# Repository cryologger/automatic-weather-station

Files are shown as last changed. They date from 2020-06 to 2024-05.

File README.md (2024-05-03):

<p align="left">



</p>

# Cryologger - Automatic Weather Station (AWS)

### Note: This project is under active development.


## 1.0 Introduction
Polar environments are undergoing rapid environmental change, yet there is a lack of high spatial and temporal monitoring data available in these remote regions. Reliance on expensive and proprietary commercial data acquisition and telemetry systems can inhibit both researchers and citizen scientists and present a significant barrier to the establishment of widespread monitoring networks. The development of low-cost, open-source instrumentation can greatly reduce the cost of cryospheric research, improve the spatial density and coverage of collected data, and produce new ways to observe and monitor the cryosphere.

The Cryologger Automatic Weather Station (AWS), is an open-source datalogger and telemeter comprised of low-cost, off the shelf components that is capable of supporting the physical measurement needs of a variety of cryospheric scientific applications when configured as an automatic weather station (AWS).

## 2.0 Methods

### 2.1 Design
The Cryologger AWS is based on the open-source Arduino platform (www.arduino.cc) and built using low-cost, do-it-yourself electronics that can be easily modified to meet the needs of the end-user. Code was written using the Arduino Integrated Development Environment (IDE) and benefits from the availability of community-generated libraries.

Planned for extended deployments in harsh Arctic conditions, the Cryologger AWS provides long-term measurements of weather variables such as temperature, humidity, wind speed, wind direction, solar irradiance and snow depth, as well as system diagnostic variables including pitch, roll, battery voltage. Data are transmitted over the Iridium satellite network at specified intervals and can be remotely updated based on the desired sampling frequency. Collected data are made available in near-real time at https://cryologger.org.



#### 2.1.1. Bill of Materials (BOM)

For a complete bill of materials, including requirements for power and mounting of a complete deployable system, please see ASSEMBLY.md.

**Table 1.** Bill of materials and associated costs for the main components used in the Cryologger AWS v1.0. Prices are listed in USD and are current as of December 2023. Taxes and shipping not included. <sup>1</sup>Denotes optional component.
| Component             | Product                                                                                                                      | Quantity | Cost (USD) |
|-----------------------|------------------------------------------------------------------------------------------------------------------------------|:--------:|:----------:|
| PCB                   | [Custom Cryologger Printed Circuit Board](https://jlcpcb.com)                                                                |     1    |    $5.00   |
| Satellite transceiver | [Rock7 RockBLOCK 9603](http://www.rock7mobile.com/products-rockblock-9603)                                                   |     1    |   $267.50  |
| Satellite antenna     | [Maxtena M1621HCT-P-SMA](https://maxtena.com/products/f-passive/m1621hct-p-sma-iridium-passive-antenna/)                     |     1    |   $54.00   |
| Processor             | [Adafruit Feather M0 Adalogger](https://www.adafruit.com/product/2796)                                                       |     1    |   $19.95   |
| GNSS                  | [Adafruit Ultimate GPS FeatherWing](https://www.adafruit.com/product/3133)                                                   |     1    |   $24.95   |
| IMU                   | [Adafruit LSM303AGR Accelerometer Magnetometer](https://www.adafruit.com/product/4413)                                       |     1    |   $12.50   |
| Sensor                | [Adafruit BME280 Temperature Humidity Pressure Sensor ](https://www.adafruit.com/product/2652)                               |     1    |   $14.95   |
| Voltage regulator     | [Pololu D36V6F3 3.3V 600mA Step-Down Voltage Regulator](https://www.pololu.com/product/3791)                                 |     1    |   $16.95   |
| Voltage regulator     | [Pololu D36V6F5 5V 600mA Step-Down Voltage Regulator](https://www.pololu.com/product/3792)                                   |     1    |   $16.95   |
| Voltage regulator     | [Pololu U3V40F12 12V Step-Up Voltage Regulator ](https://www.pololu.com/product/4016)                                        |     1    |    $9.95   |
| Resistor              | [10 M 1% 0.6 W resistor](https://www.mouser.ca/ProductDetail/594-MBB02070C1005FCT)                                           |     1    |    $0.44   |
| Resistor              | [1 M 1% 0.6 W resistor](https://www.mouser.ca/ProductDetail/594-B0207C1M000F5T)                                              |     1    |    $0.40   |
| Capacitor             | [0.1 uF Capacitor](https://www.mouser.ca/ProductDetail/Vishay-BC-Components/K104K15X7RF53L2?qs=mWFvmKOfYW8KbAXlf9eSQA%3D%3D) |     1    |    $0.29   |
| Power connector       |                                                                                                                              |     1    |            |
| Power connector       |                                                                                                                              |     1    |            |
| Connector             |                                                                                                                              |     1    |            |

**Table 2.** Environmental sensors used in Cryologger AWS v1.0. Prices are listed in USD and are current as of December 2023. Taxes and shipping not included.
| Environment Variable          | Sensor                                                                                                                       | Cost (USD) |
|-------------------------------|------------------------------------------------------------------------------------------------------------------------------|:----------:|
| Wind Speed & Direction        | [RM Young Wind Monitor 5103L Anemometer](https://www.youngusa.com/product/wind-monitor/)                                     | $1432      |
| Temperature/Relative Humidity | [Vaisala HMP60 Humidity and Temperature Probe](https://store.vaisala.com/en/products/HMP60)                                  | $330       |
| Solar Irradiance              | [SP-212-SS: Amplified 0-2.5 Volt Pyranometer](https://www.apogeeinstruments.com/sp-212-ss-amplified-0-2-5-volt-pyranometer/) | $325       |
| Snow Depth                    | [Maxboxtix MB7374 HRXL-MaxSonar-WRST7](https://maxbotix.com/products/mb7374)                                                 | $290       |

### 2.2 Operation
When initially powered on, the Cryologger AWS will attempt to establish a GNSS fix and sychronize the real-time clock (RTC) for up to 5 minutes. Once the RTC is synchronized, the system will set an alarm to wake at the user-specified time and then enter a low-power deep sleep. Nominally, the system will wake every 5 minutes, obtain measurements from all sensors, and log data to a microSD card. Measurements are averaged each hour and transmitted  

While the system is in deep sleep, a Watchdog Timer (WDT) will wake the system to check the program has not frozen every 8 seconds and perform a reset, if necessary. This helps to ensure the long-term reliability of the system.

#### 2.2.1 Measurements

**Table 2.** List of Cryologger AWS v1.0 data variables that can be transmitted and/or logged with variable sizes.

| Type     | Variable          | Description                        | Size (bytes) |
|----------|-------------------|------------------------------------|:------------:|
| uint32_t | unixtime          | UNIX Epoch time                    |       4      |
| int16_t  | temperatureInt    | Internal temperature (°C)          |       2      |
| uint16_t | humidityInt       | Internal humidity (%)              |       2      |
| uint16_t | pressureInt       | Internal pressure (hPa)            |       2      |
| int16_t  | temperatureExt    | External temperature (°C)          |       2      |
| uint16_t | humidityExt       | External humidity (%)              |       2      |
| int16_t  | pitch             | Pitch (°)                          |       2      |
| int16_t  | roll              | Roll (°)                           |       2      |
| uint16_t | solar             | Solar irradiance (W m-2)           |       2      |
| uint16_t | windSpeed         | Mean wind speed (m/s)              |       2      |
| uint16_t | windDirection     | Mean wind direction (°)            |       2      |
| uint16_t | windGustSpeed     | Wind gust speed (m/s)              |       2      |
| uint16_t | windGustDirection | Wind gust direction (°)            |       2      |
| int32_t  | latitude          | Latitude (DD)                      |       4      |
| int32_t  | longitude         | Longitude (DD)                     |       4      |
| uint8_t  | satellites        | Number of satellites               |       1      |
| uint16_t | hdop              | HDOP                               |       2      |
| uint16_t | voltage           | Battery voltage (V)                |       2      |
| uint16_t | transmitDuration  | Previous transmission duration (s) |       2      |
| uint8_t  | transmitStatus    | Iridium return code                |       1      |
| uint16_t | iterationCounter  | Message counter                    |       2      |

#### 2.2.2 Data Transmission and Processing

Sensor measurements and GNSS position are recorded hourly and stored in memory until the desired transmission interval is reached. Data are compressed into a binary message (340 bytes maximum) to minimize the cost and total number of transmissions required. Data are transmitted via the Iridium Short Burst Data (SBD) satellite network at user-specified intervals, which can be remotely updated based on the desired sampling frequency. SBD data messages are received by an Iridium ground station and sent to Ground Control's server. The data is then forwarded to an Amazon Web Services (AWS) SQS queue, decoded using an AWS Lambda Python function and stored in a database using the Amazon Relational Database Service (RDS). Data can be viewed in near-real time at https://cryologger.org.

## 3.0 Deployments


<p align="center"><b>Figure 3.</b> Map of Cryologger AWS deployments made between 2019 and 2023.</p>

## 4.0 Results

## 5.0 Conclusion

## Repository Contents

* **/Documentation** - Assembly, deployment and troubleshoting guides, as well as information of components used and associated costs.

* **/Hardware** - KiCad PCB schematic and design files.

* **/Software** - Arduino code and Python data analysis scripts.

## License Information
Cryologger code, firmware, and software is licensed under the GNU General Public License v3.0 (https://www.gnu.org/licenses/gpl-3.0.en.html). 

<p xmlns:cc="http://creativecommons.org/ns#" >Cryologger hardware is licensed under <a href="https://creativecommons.org/licenses/by-nc-sa/4.0/?ref=chooser-v1" target="_blank" rel="license noopener noreferrer" style="display:inline-block;">CC BY-NC-SA 4.0 </a></p>

Cheers,

**Adam**

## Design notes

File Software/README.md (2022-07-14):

# Cryologger - Automatic Weather Station: Software

## Repository Contents

* **/Arduino** - Code uploaded to the Cryologger to power the weather station.
* **/Python** - Python code used for analysis of weather data collected by the Cryologger.

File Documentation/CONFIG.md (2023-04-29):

## Sensor Configuration

### Vaisala HMP60

| Pin | Wire  | Description   | Description                    | Connector |
|:---:|:-----:|---------------|--------------------------------|:---------:|
| 1   | Brown | VDC           | Voltage Input (5-28V)          | 12V       |
| 2   | White | Channel 1: RH | Relative Humidity (%) (0-2.5V) | A3        |
| 3   | Blue  | GND           | Ground                         | GND       |
| 4   | Black | Channel 2: T  | Temperature (°C) (0-2.5V)      | A4        |
| 5   | Shield | Earth ground |                                | GND       |

#### HMP60 Configuration
See section 6.4 of the Vaisala Humidity and Temperature Probes User Guide:  
**Accessing serial line command interface from analog or Modbus mode**
https://docs.vaisala.com/r/M211060EN-L/en-US

```
# Show current output modes of analog channels
amode

# Set output modes of channels 1 & 2 to 0 - 2.5 V
amode 1 1 

# Show current output parameters and scaling
asel ?

# Change channel 1 to output relative humidity and adjust scaling to 0 to 100% and change channel 2 to temperature and adjust scaling to -60 to 40°C
asel rh t 0 100 -60 40

# Note: This can also be achieved by typing the asel command and entering values when prompted
asel

```

### RM Young 5103L Wind Monitor
| Pin | Wire   | Description                         | Connector |
|:---:|:------:|-------------------------------------|:---------:|
| 1   | White  | 12-30 VDC Input (Wind direction +)  | 12V       |
| 2   | Green  | 4-20 mA Output  (Wind direction -)  | A2        |
| 3   | Black  | 12-30 VDC Input (Wind speed +)      | 12V       |
| 4   | Red    | 4-20 mA Output  (Wind speed -)      | A1        |
| 5   | Shield | Earth ground                        | GND       |

### LSM303AGR
Orientation of sensor, when viewing enclosure from the front:

**Pitch:**
* Positive values (+) = Upwards (↑)
* Negative values (-) = Downwards (↓)

**Roll:**
* Positive values (+) = Left (←)
* Negative values (-) = Right (→)

## Amazon Web Services (AWS) Configuration

### Data Transmission Format

| Type     | Variable          | Description                    | Bytes | Encoding formula |
|----------|-------------------|--------------------------------|-------|------------------|
| uint32_t | unixtime          | UNIX Epoch time                | 4     |                  |
| int16_t  | intTemperature    | Internal temperature (°C)      | 2     | * 100            |
| int16_t  | extTemperature    | External temperature (°C)      | 2     | * 100            |
| uint16_t | extHumidity       | External humidity (%)          | 2     | * 10             |
| int16_t  | pitch             | Pitch (°)                      | 2     | * 100            |
| int16_t  | roll              | Roll (°)                       | 2     | * 100            |
| uint16_t | windSpeed         | Wind speed (m/s)               | 2     | * 100            |
| uint16_t | windDirection     | Wind direction (°)             | 2     |                  |
| uint16_t | windGust          | Wind gust speed (m/s)          | 2     | * 100            |
| uint16_t | windGustDirection | Wind gust direction (°)        | 2     |                  |
| uint16_t | voltage           | Battery voltage (V)            | 2     | * 100            |
| uint16_t | transmitDuration  | Previous transmission duration | 2     |                  |
| uint8_t  | transmitStatus    | Iridium return code            | 1     |                  |
| uint16_t | iterationCounter  | Message counter                | 2     |                  |
|          |                   |                      **Total** | **29**|                  |

### MariaDB 

```
CREATE TABLE 2022_aws_arctic_bay (id INT NOT NULL AUTO_INCREMENT PRIMARY KEY, imei BIGINT UNSIGNED, momsn INT UNSIGNED, transmit_time TEXT(24), iridium_latitude DOUBLE, iridium_longitude DOUBLE, iridium_cep DOUBLE, data TEXT(340), unixtime INT UNSIGNED, temperature_int DOUBLE, temperature_ext DOUBLE, humidity_ext DOUBLE, pitch DOUBLE, roll DOUBLE, wind_speed DOUBLE, wind_direction DOUBLE, wind_gust_speed DOUBLE, wind_gust_direction DOUBLE, voltage DOUBLE, transmit_duration SMALLINT, transmit_status TINYINT, message_counter INT UNSIGNED);
```

```
CREATE TABLE 2022_aws_pond_inlet (id INT NOT NULL AUTO_INCREMENT PRIMARY KEY, imei BIGINT UNSIGNED, momsn INT UNSIGNED, transmit_time TEXT(24), iridium_latitude DOUBLE, iridium_longitude DOUBLE, iridium_cep DOUBLE, data TEXT(340), unixtime INT UNSIGNED, temperature_int DOUBLE, temperature_ext DOUBLE, humidity_ext DOUBLE, pitch DOUBLE, roll DOUBLE, wind_speed DOUBLE, wind_direction DOUBLE, wind_gust_speed DOUBLE, wind_gust_direction DOUBLE, voltage DOUBLE, transmit_duration SMALLINT, transmit_status TINYINT, message_counter INT UNSIGNED);
```

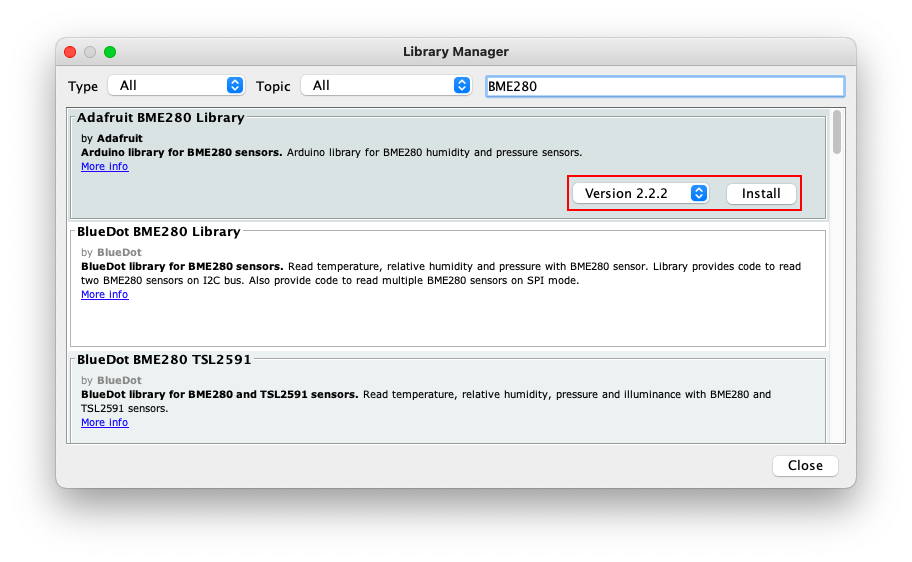
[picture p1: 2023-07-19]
Images/arduino-ide-library.png

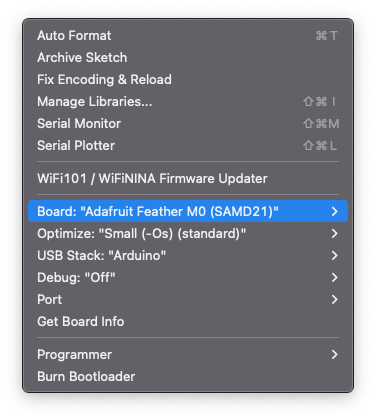
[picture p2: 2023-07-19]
Images/arduino-ide-board-1.png

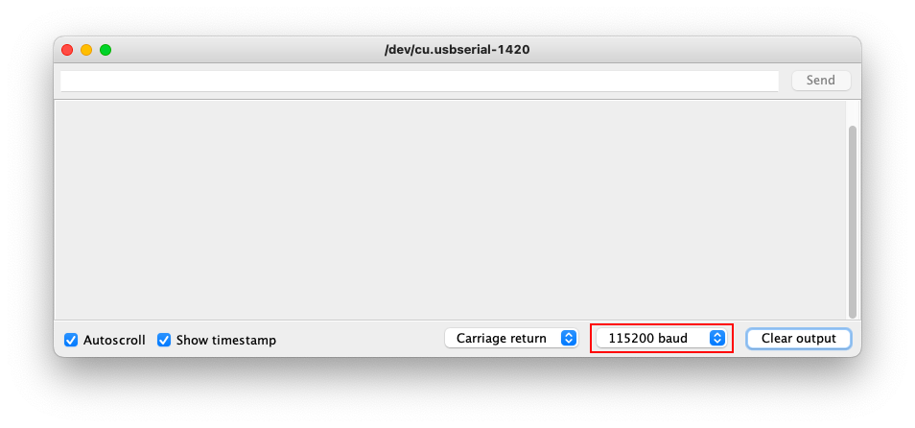
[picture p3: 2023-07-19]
Images/arduino-ide-serial-monitor-2.png

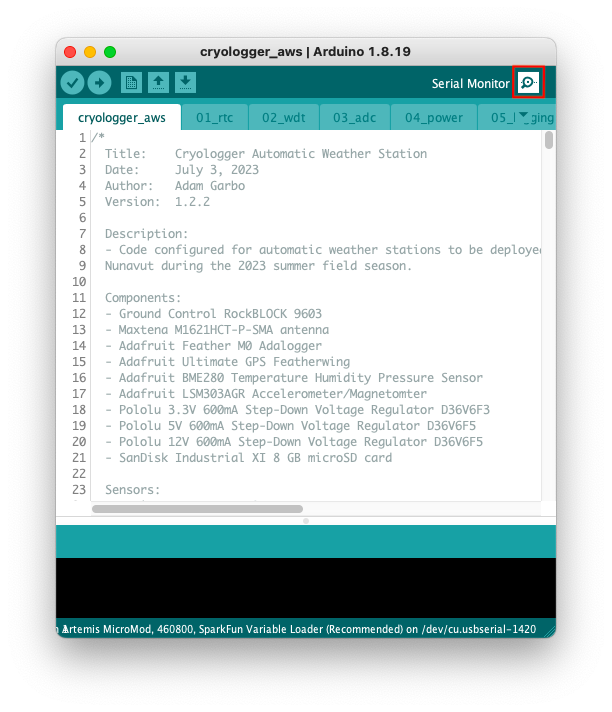
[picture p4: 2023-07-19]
Images/arduino-ide-serial-monitor-1.png

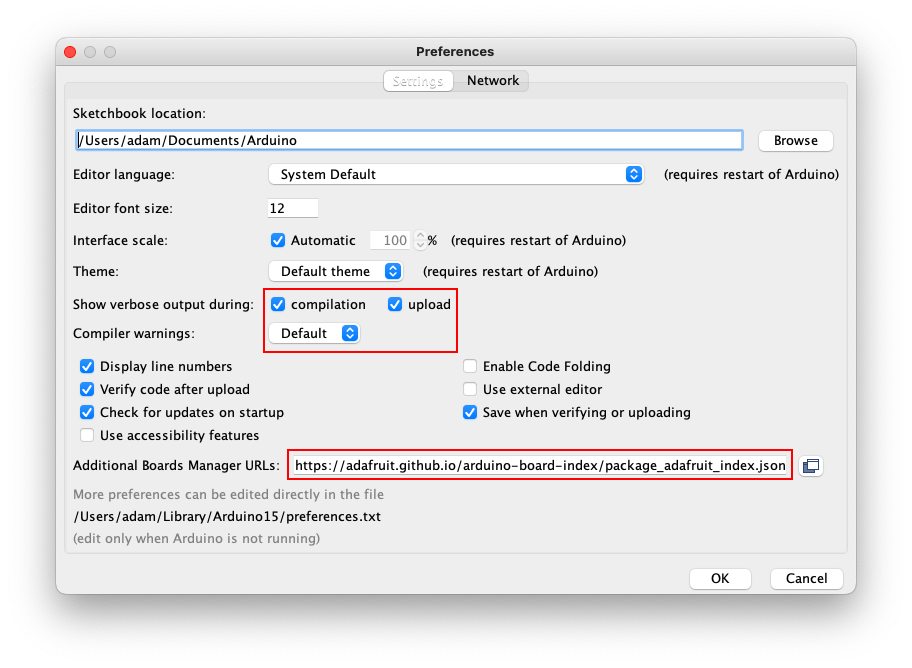
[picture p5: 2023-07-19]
Images/arduino-ide-preferences.png

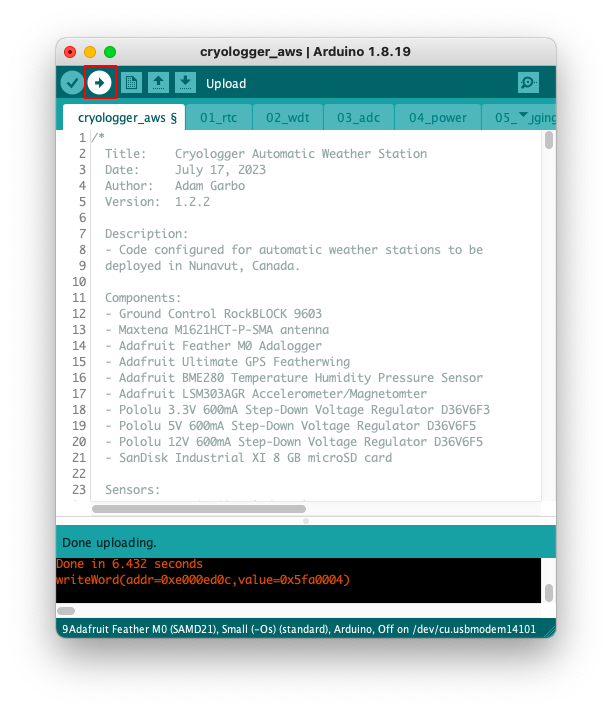
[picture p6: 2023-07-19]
Images/arduino-ide-upload.png

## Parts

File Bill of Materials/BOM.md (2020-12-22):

# Bill of Materials

| Component | Product | Cost (USD) | URL |
| --- | --- | :---: | --- |
| Satellite transceiver | Rock7 RockBLOCK 9603 | $249.95 | https://www.rock7.com/shop-product-detail?productId=51 |
| Microcontroller | Adafruit Feather M0 Adalogger | $19.95 | https://www.adafruit.com/product/2796 |
| Real-time clock | Adafruit DS3231 Precision RTC FeatherWing | $13.95 | https://www.adafruit.com/product/3028 |
| Real-time clock battery | CR1220 12mm Diameter - 3V Lithium Coin Cell Battery | $2.50 | https://www.adafruit.com/product/380 |
| Protoboard | Adafruit FeatherWing Tripler Mini Kit | $8.50 | https://www.adafruit.com/product/3417 |
| Terminal block | Adafruit Terminal Block kit for Feather - 0.1" Pitch | $5.95 | https://www.adafruit.com/product/3173 |
| Voltage Regulator | Pololu D36V6F3 3.3V 600 mA Step-Down Voltage Regulator | $4.95 | https://www.pololu.com/product/3791 |
| Power connector | Male DC Power adapter - 2.1mm plug to screw terminal block | $2.00 | https://www.adafruit.com/product/369 |
| Power connector | Breadboard-friendly 2.1mm DC barrel jack | $0.95 | https://www.adafruit.com/product/373 |
| Anemometer / Wind Vane | Davis Instruments Anemometer (#7911) | $155.00 | https://www.davisinstruments.com/product/anemometer-for-weather-monitor-or-wizard/ |
| Temperature / Relative Humidity Sensor | Davis Instruments Temperature/Humidity Sensor (#6834) | $70.00 | https://www.davisinstruments.com/product/temperature-humidity-sensor/ |
| Radiation Shield | Davis Instruments Radiation Shield (#7714) | $85.00 | https://www.davisinstruments.com/product/radiation-shield/ |
| Battery |	Tadiran	Lithium Pulses Plus 7.2V 38Ah 273.6Wh (TLP-93131/B/AL1) | $150 | http://www.tadiranbat.com/assets/tlp-93121-b-al1.pdf |
| Enclosure | Pelican 1120 | $31.95 | https://www.pelican.com/us/en/product/cases/protector/1120 |
| Total |  | $1000 | |

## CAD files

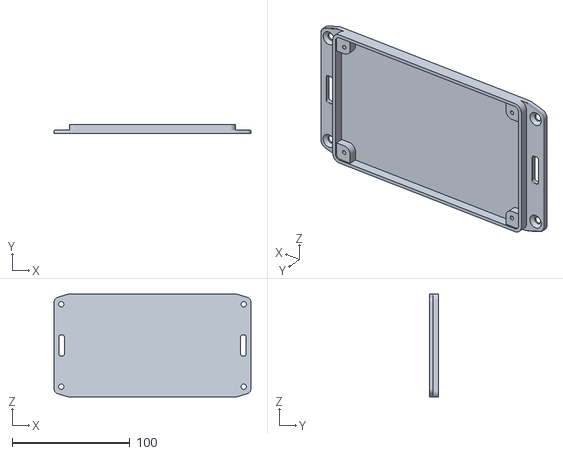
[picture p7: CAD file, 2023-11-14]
Hardware/3D Printing/Enclosure Bottom.stl
167.4 x 8.00 x 87.4

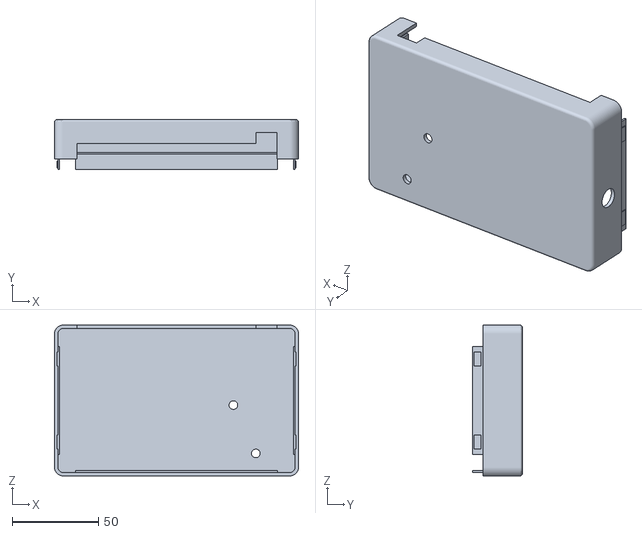
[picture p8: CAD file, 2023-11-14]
Hardware/3D Printing/Enclosure Top.stl
141.4 x 29.0 x 87.4

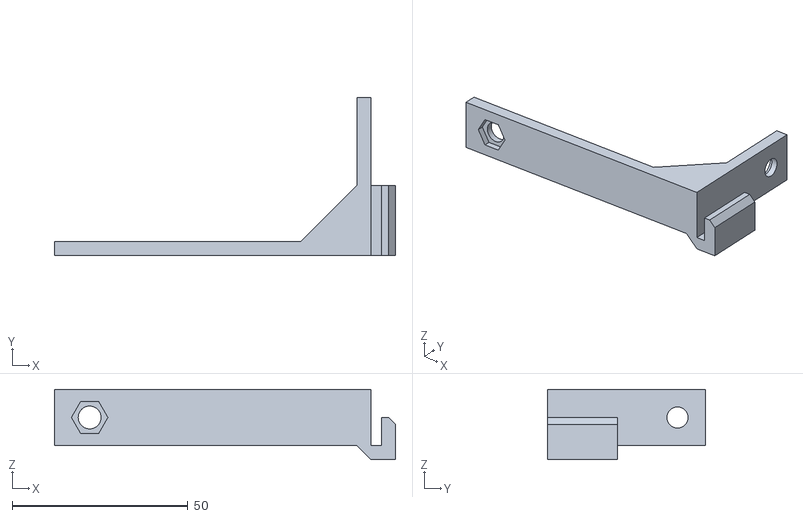
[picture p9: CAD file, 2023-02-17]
Hardware/3D Printing/Antenna Arm.stl
97.0 x 45.0 x 20.0

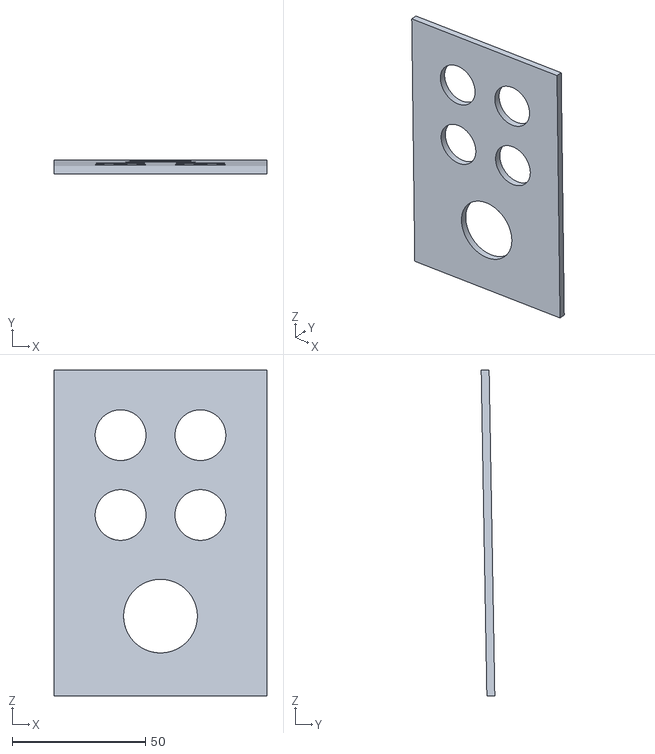
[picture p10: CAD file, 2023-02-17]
Hardware/3D Printing/Connector Panel.stl
80.0 x 5.14 x 122.5

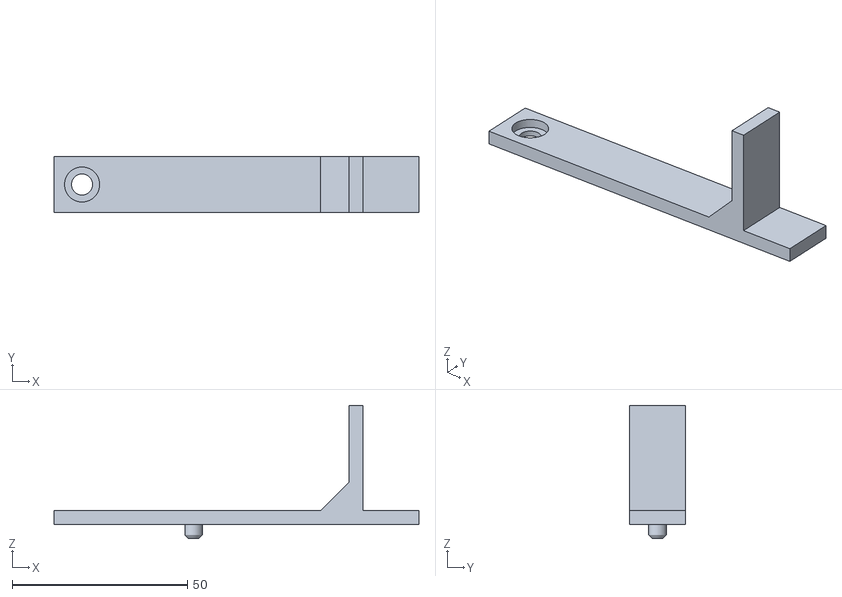
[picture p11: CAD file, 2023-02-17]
Hardware/3D Printing/Battery Bracket.stl
104.0 x 16.0 x 38.0

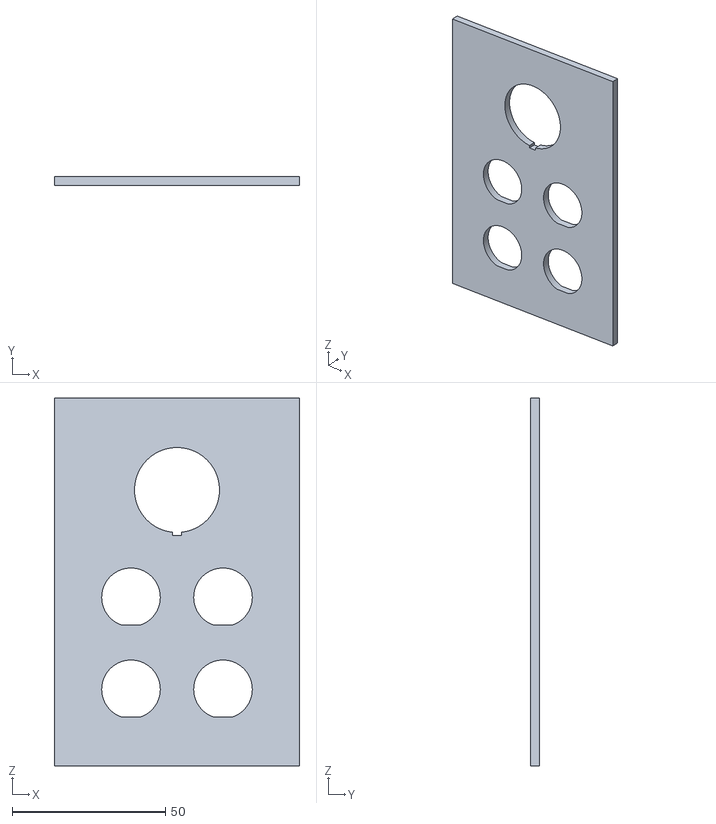
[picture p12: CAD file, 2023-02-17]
Hardware/3D Printing/Connector Panel Keyed.stl
80.0 x 3.00 x 120.0

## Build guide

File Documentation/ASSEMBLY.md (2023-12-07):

# Cryologger Automatic Weather Station (AWS) - Assembly

## 1.0 Introduction
This guide provides detailed instructions on the assembly of a Cryologger AWS v1.0.

## 2.0 Bill of Materials (BOM)
The components required to assemble a Cryologger GVT system are split into two groups: 
1) Components required for the assembly of the Cryologger AWS (e.g., PCB, GNSS receiver, microcontroller, etc.)
2) Components required for the mounting, power and deployment of the complete system (e.g., tripod, solar panel, battery, etc.).

**Table 1.** Recommended tools required for the asssembly of a Cryologger AWS v1.0.
| Tool | Recommended Product |
| --- | --- | 
| Soldering iron | [Hakko FX-888D Digital Soldering Station](https://hakkousa.com/fx-888d-digital-soldering-station.html) |
| Solder | [SparkFun Solder - 1/4lb Spool (0.020") Special Blend](https://www.sparkfun.com/products/10242) |
| Side cutter | [Hakko CHP-170 Micro Cutter](https://hakkousa.com/chp-170-micro-cutter.html) |
| Pliers | [Hakko CHP PN-2001 Pointed Nose Pliers](https://hakkousa.com/products/chp-tools/chp-hand-tools/chp-pn-2001-pointed-nose-pliers.html) |
| Hot-air rework station | [Quick 957DW+](https://www.adafruit.com/product/1869) |
| Screw driver | Phillips head screw driver |
| PCB cleaning brush | [ESD-Safe PCB Cleaning Brush](https://www.adafruit.com/product/1209) |
| PCB cleaning solution | Deionized (DI) water |

**Table 1.** Bill of materials and associated costs for components used in the Cryologger AWS v1.0. Prices are listed in USD and are current as of December 2023. Taxes and shipping not included. <sup>1</sup>Denotes optional component. Please note the BOM is a work in progress.
| Component             | Product                                                               | Cost (USD) |
|-----------------------|-----------------------------------------------------------| :---: |
| Satellite transceiver | [Rock7 RockBLOCK 9603](http://www.rock7mobile.com/products-rockblock-9603) | $267.50
| Satellite antenna*    | [Maxtena M1621HCT-P-SMA](https://maxtena.com/products/f-passive/m1621hct-p-sma-iridium-passive-antenna/) | $54.00 
| Processor             | [Adafruit Feather M0 Adalogger](https://www.adafruit.com/product/2796) | $19.95
| GNSS                  | [Adafruit Ultimate GPS FeatherWing](https://www.adafruit.com/product/3133) | $24.95
| IMU                   | [Adafruit LSM303AGR Accelerometer Magnetometer](https://www.adafruit.com/product/4413) | $12.50
| Sensor                | [Adafruit BME280 Temperature Humidity Pressure Sensor ](https://www.adafruit.com/product/2652) | $14.95
| Voltage regulator     | [Pololu D36V6F3 3.3V 600mA Step-Down Voltage Regulator](https://www.pololu.com/product/3791) | $16.95 
| Voltage regulator     | [Pololu D36V6F5 5V 600mA Step-Down Voltage Regulator](https://www.pololu.com/product/3792) | $16.95 
| Voltage regulator     | [Pololu U3V40F12 12V Step-Up Voltage Regulator ](https://www.pololu.com/product/4016) | $9.95 
| Resistor              | [10 M 1% 0.6 W resistor](https://www.mouser.ca/ProductDetail/594-MBB02070C1005FCT) | $0.44 |
| Resistor              | [1 M 1% 0.6 W resistor](https://www.mouser.ca/ProductDetail/594-B0207C1M000F5T) | $0.40 
| Capacitor             | [0.1 uF Capacitor](https://www.mouser.ca/ProductDetail/Vishay-BC-Components/K104K15X7RF53L2?qs=mWFvmKOfYW8KbAXlf9eSQA%3D%3D) | $0.29 
| Power connector       |	[Phoenix Contact MSTB 2,5/ 2-ST-5,08 - 1757019](https://www.mouser.ca/ProductDetail/Phoenix-Contact/1757242?qs=%2Fha2pyFadugVjodGKkrF4xNq%252BZEVHysqCHlL2cTnJ%252B8%3D) | $0.67 
| Power connector	      | [Phoenix Contact MSTBA 2,5/ 2-G-5,08 - 1757242](https://www.mouser.ca/ProductDetail/Phoenix-Contact/1757019?qs=sGAEpiMZZMvlX3nhDDO4AGmxTE5dWGQY3FmaBdjJUN0%3D) | $2.08 
| Connector             |	[Molex PicoBlade PCB Header](https://www.mouser.ca/datasheet/2/276/0530471010_PCB_HEADERS-171035.pdf) | $0.50 

**Table x.** Sensors
| Environment Variable          | Sensor                                                                                         | Cost (USD) |
|-------------------------------|------------------------------------------------------------------------------------------------|:----------:|
| Wind Speed & Direction        | [RM Young Wind Monitor 5103L Anemometer](https://www.youngusa.com/product/wind-monitor/)       | $1432      |
| Temperature/Relative Humidity | [Vaisala HMP60 Humidity and Temperature Probe](https://store.vaisala.com/en/products/HMP60)    | $330       |
| Solar Irradiance              | [SP-212-SS: Amplified 0-2.5 Volt Pyranometer](https://www.apogeeinstruments.com/sp-212-ss-amplified-0-2-5-volt-pyranometer/) | $325       |
| Snow Depth                    | [Maxboxtix MB7374 HRXL-MaxSonar-WRST7](https://maxbotix.com/products/mb7374)                   | $290       |

**Table 3.** Components making up the enclosure, mounting and power systems for Cryologger AWS v1.0. <sup>1</sup>Denotes optional component. <sup>2</sup>Denotes educational pricing.
| Component | Product | Quantity | Cost (USD) | 
| --- | --- | :---: | :---: | 
| Solar Panel | [Ameresco Solar 20 Watt Solar Panel 20J<sup>2</sup>](https://www.amerescosolar.com/20j-ameresco-solar-20-watt-solar-panel) | 1 |  $99.00 |
| Solar Panel Bracket | [Ameresco Solar HPM18-30 Solar Panel Pole Mount<sup>2</sup>](https://www.amerescosolar.com/hpm18-30solar-panel-pole-mount) | 1 |  $39.00 
| Solar Charge Controller | [Genasun GV-4 4A MPPT Solar Charge Controller](https://www.altestore.com/store/charge-controllers/solar-charge-controllers/mppt-solar-charge-controllers/genasun-gv-4-pb-12v-4a-mppt-controller-for-12v-lead-acid-batteries-p10622/) | 1 |  $63.00 |
| Solar Panel Power Cable | [Polarwire Arctic Ultraflex Blue Twin Trailer Cable AUF-TC162](https://store.polarwire.com/arctic-trailer-cable-16-2-gray-16ga-2-conductors/) | Variable | $0.55/ft |
| Solar Panel Cable Gland | [Heyco M4340 M20 Cable Gland](https://octopart.com/m4340-heyco-2298364?r=sp) | 2 | $5.94 |
| Battery Ring Terminal | [Molex Perma-Seal Ring Terminal 14-16 AWG Wire 1/4" (M6) 19164-0026](https://octopart.com/19164-0026-molex-99569?r=sp) | 2 | $1.00 |
| Battery | Deka SOLAR Gel 48 Ah 8G40C | 1 | ~$150.00 |
| Antenna Bulkhead Adapter | [Amphenol TNC Jk to TNC Jk 50 Ohm Str Bkhd IP67 AD-TNCJTNCJ-1](https://octopart.com/ad-tncjtncj-1-amphenol+rf-108109770?r=sp) | 1 | $42.79 |
| Antenna Cable | [GPAC GPS Antenna Cable TNC to TNC (3 m)](https://www.gpac-llc.com/product.php?product=1) | 1 | $56.00 |
| Enclosure | [L-Com 14x12x7 Inch Weatherproof NEMA Enclosure](https://www.l-com.com/nema-enclosures-14x12x7-inch-weatherproof-nema-enclosure-only) | 1 |  $161.99 |
| Enclosure Panel | [L-Com Blank Aluminum Mounting Plate](https://www.l-com.com/nema-enclosures-blank-aluminum-mounting-plate-for-1412xx-series-enclosures) | 1 |  $32.39 |
| Pole Mount | [L-Com Enclosure Pole Mounting Kit](https://www.l-com.com/nema-enclosures-enclosure-pole-mounting-kit-pole-diameters-1-1-4-to-2-inches) | 1 | $75.99 |
| Tripod | [Onset HOBO Weather Station m 3m Tripod M-TPA](https://www.onsetcomp.com/products/mounting/m-tpa/) | 1 |  $200.00 | 

## 3.0 Assembly

### 3.1 Cryologger AWS PCB Assembly
**1) Collect all required components**
* It is suggested to first gather all of the components listed in the bill of materials (Table 2), required for the assembly of the Cryologger. Remove the components from their packaging and inspect them for any signs of damage.

**2) Solder through-hole resistors and capacitor**
* The first components recommended to be soldered to the Cryologger PCB are the through-hole resistors and capacitor (Figure 1). 
* Both the capacitor and resistors can be inserted into the PCB in any orientation.
* It is important to pay attention to the placement of the resistors, as they differ in resistance. 
  * R1 = 10 MOhm. Colour code: Brown Black Black Green Brown
  * R2 = 1 MOhm. Colour code: Brown Black Black Yellow Brown
* For more information on resistance colour codes, please see: https://www.digikey.com/en/resources/conversion-calculators/conversion-calculator-resistor-color-code

## 4.0 Calibration

## 5.0 Testing

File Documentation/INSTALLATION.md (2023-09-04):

# Cryologger Automatic Weather Station (AWS) - Installation
This guide provides step-by-step instructions on installing the Arduino IDE and required board definitions and libraries, which are necessary for uploading code to the Cryologger AWS.

## Step 1: Download Arduino IDE  
* Navigate to https://www.arduino.cc/en/software and download the Legacy 1.8.x version of the Arduino IDE
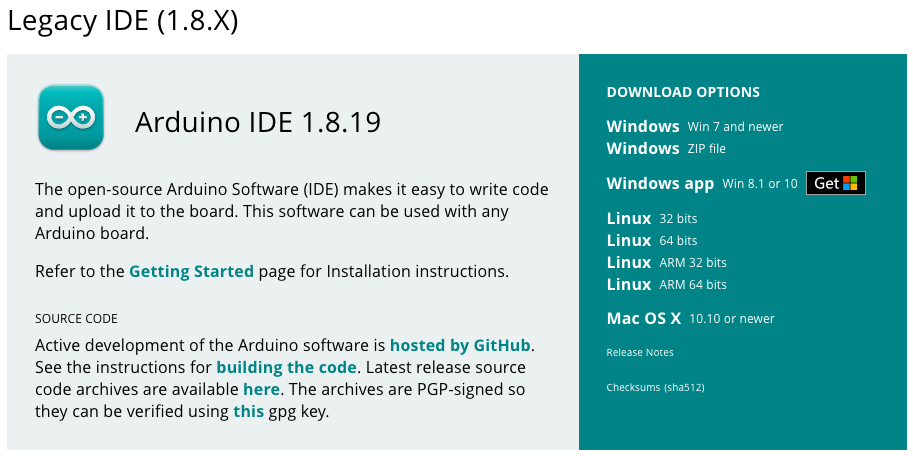
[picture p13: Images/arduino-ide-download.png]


## Step 2: Add Additional Boards Manager URL:
* In the Arduino IDE navigate to: Preferences
* Add the following "Additional Boards Manager URL" as shown in the screenshot below:  
```https://adafruit.github.io/arduino-board-index/package_adafruit_index.json```
* Also during this step, check the "compile" and "upload" boxes for "Show verbose output during" and change "Compiler warnings" to "Default"
![image](/Images/arduino-ide-preferences.png)

## Step 3: Install Board Definitions
* Navigate to: Tools > Boards > Boards Manager
* Search for: SAMD Boards
* Select and install version: Arduino SAMD Boards v1.8.13 
* Select and install version: Adafruit SAMD Boards v1.7.13
![image](/Images/arduino-ide-boards.png)

## Step 4: Install Libraries
Several libraries are required by the Cryologger AWS. These can be downloaded using the Arduino IDE's Library Manager (requires an Internet connection).

* Navigate to: Tools > Manage Libraries
* Search for and install the following libraries:

**Table 1.** Libraries required by Cryologger AWS. Last updated 2023-07-01.
| Library                                         | Version | GitHub Repository                                                   |
|-------------------------------------------------|:-------:|---------------------------------------------------------------------|
| Adafruit BME280 Library                         |  2.2.2  | https://github.com/adafruit/Adafruit_BME280                         |
| Adafruit LSM303 Accelerometer Library           |  1.1.6  | https://github.com/adafruit/Adafruit_LSM303_Accel                   |
| Adafruit Unified Sensor Driver                  |  1.1.9  | https://github.com/adafruit/Adafruit_Sensor                         |
| Arduino Low Power Library                       |  1.2.2  | https://github.com/arduino-libraries/ArduinoLowPower                |
| SparkFun IridiumSBD I2C Arduino Library         |  3.0.6  | https://github.com/sparkfun/SparkFun_IridiumSBD_I2C_Arduino_Library |
| RTCZero Library                                 |  1.6.0  | https://github.com/arduino-libraries/RTCZero                        |
| SdFat                                           |  2.2.2  | https://github.com/greiman/SdFat                                    |
| Sensirion Temperature / Humidity Sensor Library |         | https://github.com/HydroSense/sensirion                             |
| Statistic Library                               |  1.0.4  | https://github.com/RobTillaart/Statistic                            |
| Arduino Time Library                            |  1.6.1  | https://github.com/PaulStoffregen/Time                              |
| TinyGPSPlus                                     |  1.0.3  | https://github.com/mikalhart/TinyGPSPlus                            |

![image](/Images/arduino-ide-library.png)

## Step 5: Download Software
Code for the Cryologger AWS is made available on the following GitHub repository:
* [https://github.com/adamgarbo/Cryologger Automatic Weather Station](https://github.com/adamgarbo/Cryologger_Automatic_Weather_Station)
* Click on "Releases" and download the .zip file of the most recent release:
![image](https://github.com/adamgarbo/cryologger-automatic-weather-station/assets/22924092/7f80eec5-b06e-466e-aa5a-90dcd1c81258)

## Step 6: Test Program Compilation
* Navigate to the /Software/Arduino/cryologger_aws folder of the downloaded repository
* Double-click on the `cryologger_aws.ino` file
* Click on the checkmark in the upper left corner of the Arduino IDE program window
* Watch debugging window for compilation errors

![image](/Images/arduino-ide-verify.png)

## Step 7: Connect Hardware & Configure Port Settings
* Connect to the Cryologger AWS using a micro USB cable.
* In the Arduino IDE click on Tools > Board > Adafruit SAMD > Adafruit Feather M0 (SAMD)

![image](/Images/arduino-ide-board-1.png)
![image](/Images/arduino-ide-board-2.png)
![image](/Images/arduino-ide-board-3.png)

* Next, click on Tools > Port and select the appropriate serial port for the Adafruit Feather M0 Adalogger
![image](/Images/arduino-ide-port-1.png)
![image](/Images/arduino-ide-port-2.png)

## Step 8: Upload Program
* Once the code has compiled successfully, click on the right-pointed arrow to upload the code
* Watch the output window for compilation errors and/or success messages
* If no errors are presented, the code has now been successfully uploaded! 
![image](/Images/arduino-ide-upload.png)

## Step 9: Observe Serial Monitor
* After successfully uploading the program, click on the magnifying glass in the top right-hand corner to open the Serial Monitor
* Click on the baud dropdown and select 115200 baud
* Ensure the data logging mode and settings are correct
![image](/Images/arduino-ide-serial-monitor-1.png)
![image](/Images/arduino-ide-serial-monitor-2.png)

## Step 10: Next Steps
* The detailed operation of the Cryologger AWS will be covered next in OPERATION.md

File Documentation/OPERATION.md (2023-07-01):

# Cryologger Automatic Weather Station (AWS) - Operation

## Wiring Diagram

**Table 1.** Davis Instruments 7911 anemometer.
| Wire   | Description    | Pin |
|--------|----------------|-----|
| Black  | Wind speed     | A1  |
| Red    | Ground         | GND |
| Green  | Wind direction | A2  |
| Yellow | Power          | U3  |

**Table 2.** Davis Instruments temperature relative humidity sensor (Sensiron SHT31-LSS).
| Wire   | Description | Pin |
|--------|-------------|-----|
| Blue   | Data        | SDA |
| Yellow | Power       | 3.3 |
| Green  | Ground      | GND |
| White  | Clock       | SCL |

**Table 3.** Wiring diagram for Apogee SP-212 pyranometer.
| Wire   | Description | Pin |
|--------|-------------|-----|
| Black  | Ground      | GND |
| White  | Sensor      | A3  |
| Red    | Power       | 5V  |
| Shield | Shield      | GND |

**Table 4.** Wiring diagram for MaxBotix MB7354 HRXL-MaxSonar-WRS5 ultrasonic sensor.
| Wire Colour |      Description      |      Pin      |
|:-----------:|:---------------------:|:-------------:|
|    White    |   Temperature Sensor  | Not connected |
|    Orange   |   Pulse Width Output  |       A3      |
|    Brown    | Analog Voltage Output | Not connected |
|    Green    |   Ranging Start/Stop  | Not connected |
|     Blue    |     Serial Output     | Not connected |
|     Red     |          Vcc          |       5V      |
|    Black    |         Ground        |      GND      |

## LED Blink Patterns

When initially powered on, the system will attempt to establish a GNSS fix and synchronize the real-time clock (RTC) for up to 2 minutes. During this time, the LED will blink every second. Once the RTC is synchronized, the system will set an alarm to wake at the user-specified time and then enter a low-power deep sleep. While the system is in deep sleep, the Watchdog Timer (WDT) will wake the system to check the program has not frozen approximately every 8 seconds. The LED will blink briefly (100 ms) during this time.

Table x. LED blink patterns and associated description and troubleshooting guide.
| Number | Duration (ms) |    Colour   |   Pattern   | Description                     | Troubleshooting Steps                     |
|:------:|:-------------:|:-----------:|:-----------:|---------------------------------|-------------------------------------------|
|    4   |      500      |     Red     |   Single    | System start up                 | None                                      |
|   10   |      100      | Green + Red | Alternating | Initialization complete         | None                                      |
|    2   |      250      |     Red     |  Continuous | microSD failure                 | Reseat microSD card and reboot system     |
|    1   |      1000     |    Green    |  Continuous | GNSS signal acquisition         | None                                      |
|    5   |      100      |    Green    |   Single    | GNSS fix found                  | None                                      |
|    5   |      100      |     Red     |   Single    | GNSS fix not found              | Ensure good view of sky                   |
|    1   |      1000     |    Green    |  Continuous | Iridium transmission attempt    | None                                      |
|   10   |      250      |    Green    |   Single    | Iridium transmission successful | None                                      |
|   10   |      250      |     Red     |   Single    | Iridium transmission failure    | Ensure good view of sky and reboot system |
|    1   |      100      |     Red     |   Single    | Watchdog Timer every 8 seconds  | None                                      |

## Tools
| Component                             	| Type                       	| Tool(s)                             	|
|---------------------------------------	|----------------------------	|-------------------------------------	|
| Enclosure panel                       	| 10/32" 3/8" Pan Head Screw 	| Phillips Head Screwdriver (large)   	|
| Enclosure pole mount bracket          	| 1/4"-20 Pan Head Screw     	| Phillips Head Screwdriver (large)   	|
| Enclosure pole mount bracket          	| 1/4"-20 Hex Nut            	| 7/16" socket/wrench                 	|
| Enclosure pole mount bracket u-bolt   	| 1/4"-20 Hex Nut            	| 7/16" socket/wrench                 	|
| Radiation shield                      	| 1/4"-20 Locknut            	| 7/16" socket                        	|
| Solar panel 1 3/4" u-bolt             	| 5/16"-18 Hex Nut           	| 1/2" wrench/socket                  	|
| Polar Wire cable                      	| 14 AWG                     	| Wire stripper                       	|
| Genasun GV-4 Solar charge controller  	| Screw terminal             	| Flat head (small)                   	|
| Deka 8GUIH battery terminals          	| 1/4"-20 Hex Nut            	| 7/16" socket/wrench                 	|
| Anemometer 1-3/4" & 1-5/8" u-bolts    	| 5/16"-18 Hex Nut           	| 1/2" socket/wrench                  	|
| Anemometer stainless steel hose clamp 	| Screw                      	| Phillips Head Screwdriver  (medium) 	|
| Anemometer stainless steel hose clamp 	| Nut                        	| 5/16" socket (optional)             	|
| Tripod 1-3/4" u-bolt                  	| 5/16"-18 Hex Nut           	| 1/2" socket/wrench                  	|
| Tripod 1-5/8" u-bolt                  	| 1/4"-20 Hex Nut            	| 7/16" socket/wrench                 	|
| Tripod guy wire kit                   	| Cable                      	| Lineman Cutters                     	|
| Tripod guy wire kit                   	| 10/32" 3/8" Pan Head Screw 	| Phillips Head Screwdriver (medium)  	|
| Tripod guy wire kit                   	| 1/4"-20 Hex Nut            	| 7/16" socket                        	|
| Tripod guy wire kit                   	| 5/16"-18 Hex Nut           	| 1/2" wrench                         	|
| PCB Screw terminals                   	| Screw terminal             	| Flat head (small)                   	|

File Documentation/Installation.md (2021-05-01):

# Installation

## Arduino IDE

Download the most recent version of the Arduino Software (IDE) from:
https://www.arduino.cc/en/main/software

### Custom Board Manager URLs:

To make use of SparkFun and Adafruit flavoured boards, it is necessary to first add their Additional Boards Manager URLs. These are JSON URLs added as a comma-separated list in Preferences of the Arduino IDE.

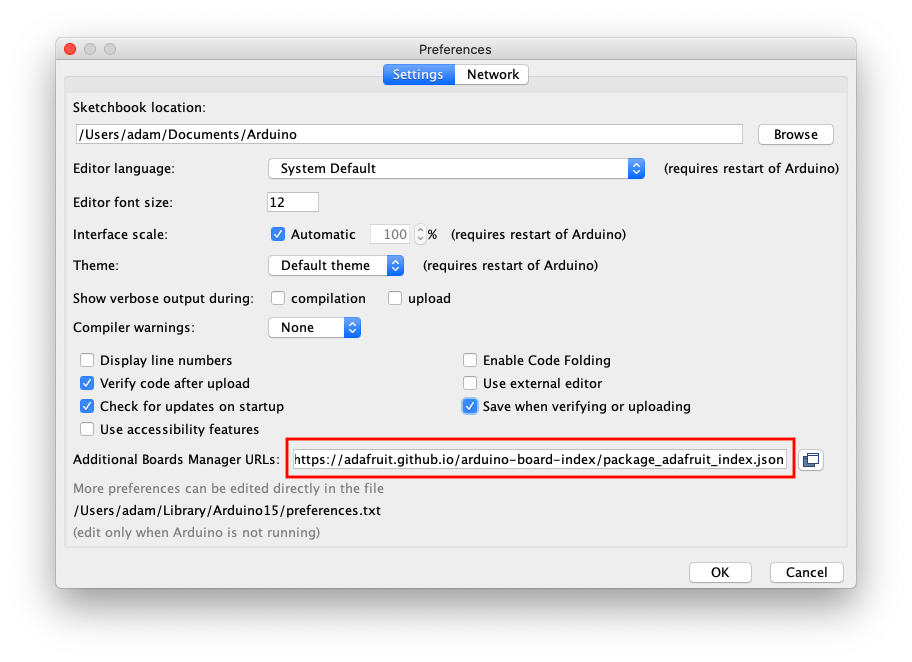
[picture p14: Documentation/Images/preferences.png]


**Adafruit:** 
* **Guide:** https://learn.adafruit.com/add-boards-arduino-v164/setup
* **URL:** `https://adafruit.github.io/arduino-board-index/package_adafruit_index.json`

**SparkFun:**
* **Guide:** https://learn.sparkfun.com/pages/CustomBoardsArduino
* **URL:** `https://raw.githubusercontent.com/sparkfun/Arduino_Boards/master/IDE_Board_Manager/package_sparkfun_index.json`

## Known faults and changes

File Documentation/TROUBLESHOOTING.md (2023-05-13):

## RM Young 5103L Wind Monitor

### Wiring

| Pin | Wire   | Description                         | Connector |
|:---:|:------:|-------------------------------------|:---------:|
| 1   | White  | 12-30 VDC Input (Wind direction +)  | 12V       |
| 2   | Green  | 4-20 mA Output  (Wind direction -)  | A2        |
| 3   | Black  | 12-30 VDC Input (Wind speed +)      | 12V       |
| 4   | Red    | 4-20 mA Output  (Wind speed -)      | A1        |
| 5   | Shield | Earth ground                        | GND       |

### Troubleshooting

| Scenario       | Wind Speed (Analog) | Wind Direction (Analog) | Wind Speed (m/s) | Wind Direction (°) | Comments      |
|----------------|:-------------------:|:-----------------------:|:----------------:|:------------------:|---------------|
| Disconnect 12V |          4          |            3            |      -25.21      |       -90.89       | Floating      |
| Disconnect WD+ |          0          |            -            |      -25.21      |          -         | Floating      |
| Disconnect WD- |          -          |            0            |         -        |       -90.89       | Floating      |
| Unplug battery |          0          |            0            |      -25.21      |       -90.89       | Floating      |

## Vaisala HMP60

### Wiring
| Pin | Wire  | Description   | Description                    | Connector |
|:---:|:-----:|---------------|--------------------------------|:---------:|
| 1   | Brown | VDC           | Voltage Input (5-28V)          | 12V       |
| 2   | White | Channel 1: RH | Relative Humidity (%) (0-2.5V) | A3        |
| 3   | Blue  | GND           | Ground                         | GND       |
| 4   | Black | Channel 2: T  | Temperature (°C) (0-2.5V)      | A4        |
| 5   | Shield | Earth ground |                                | GND       |

### Troubleshooting

| Scenario                           | Temperature (Analog) | Humidity (Analog) | Temperature (°C) | Humidity (%) | Comments      |
|------------------------------------|:--------------------:|:-----------------:|:----------------:|:------------:|---------------|
| Disconnect 12V                     |        287-416       |      288-417      |       ~-55       |      ~10     | Floating      |
| Disconnect GND                     |         3286         |        3241       |        >40       |     >100     | Max ADC value |
| Disconnect Channel 1 (Humidity)    |           -          |        1550       |         -        |      50      | Floating      |
| Disconnect Channel 2 (Temperature) |         1550         |         -         |        -10       |       -      | Floating      |
| Unplug M12 connector               |         ~1550        |       ~1550       |        -10       |      50      | Floating      |
| Unplug battery                     |          10          |         10        |        -60       |       0      | Min ADC value |

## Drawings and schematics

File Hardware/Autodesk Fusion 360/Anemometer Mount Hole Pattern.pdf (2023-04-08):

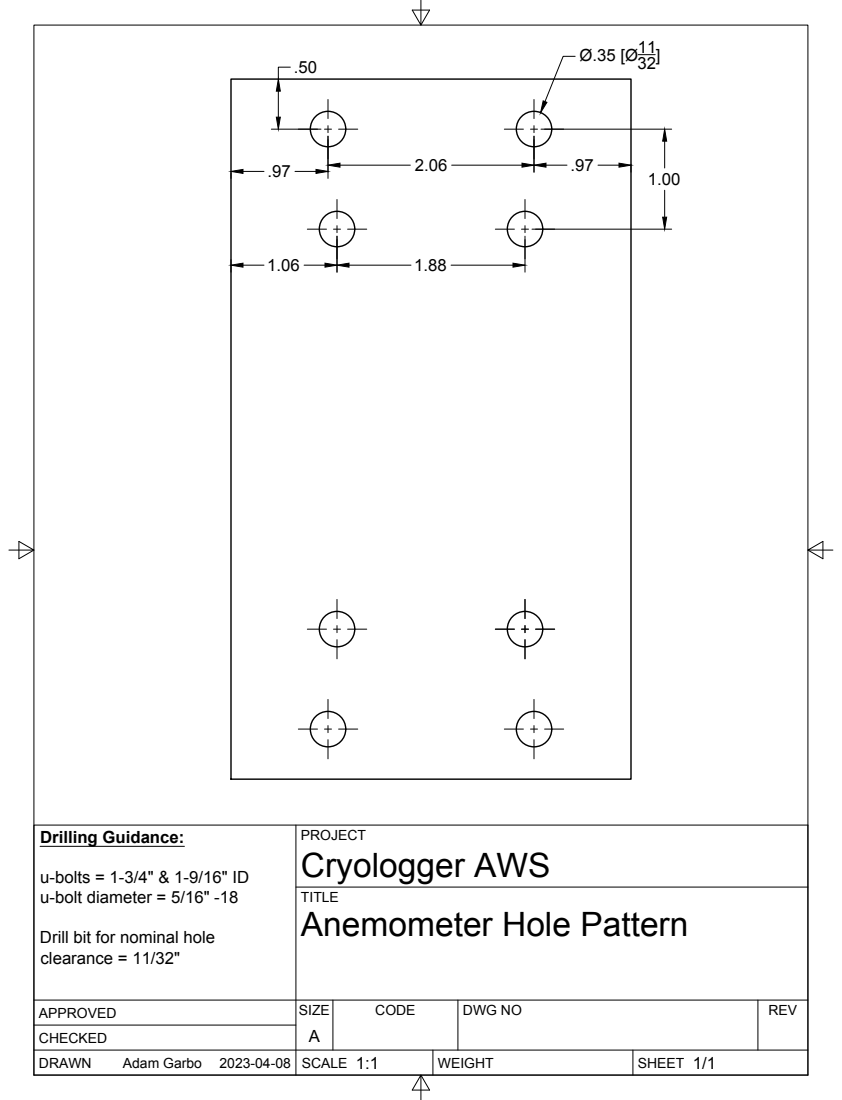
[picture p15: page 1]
SIZE; CODE; DWG NO; REV; Adam Garbo; Drilling Guidance:; u-bolts = 1-3/4" & 1-9/16" ID u-bolt diameter = 5/16" -18

PROJECT
Cryologger AWS
Anemometer Hole Pattern

Drill bit for nominal hole
clearance = 11/32"

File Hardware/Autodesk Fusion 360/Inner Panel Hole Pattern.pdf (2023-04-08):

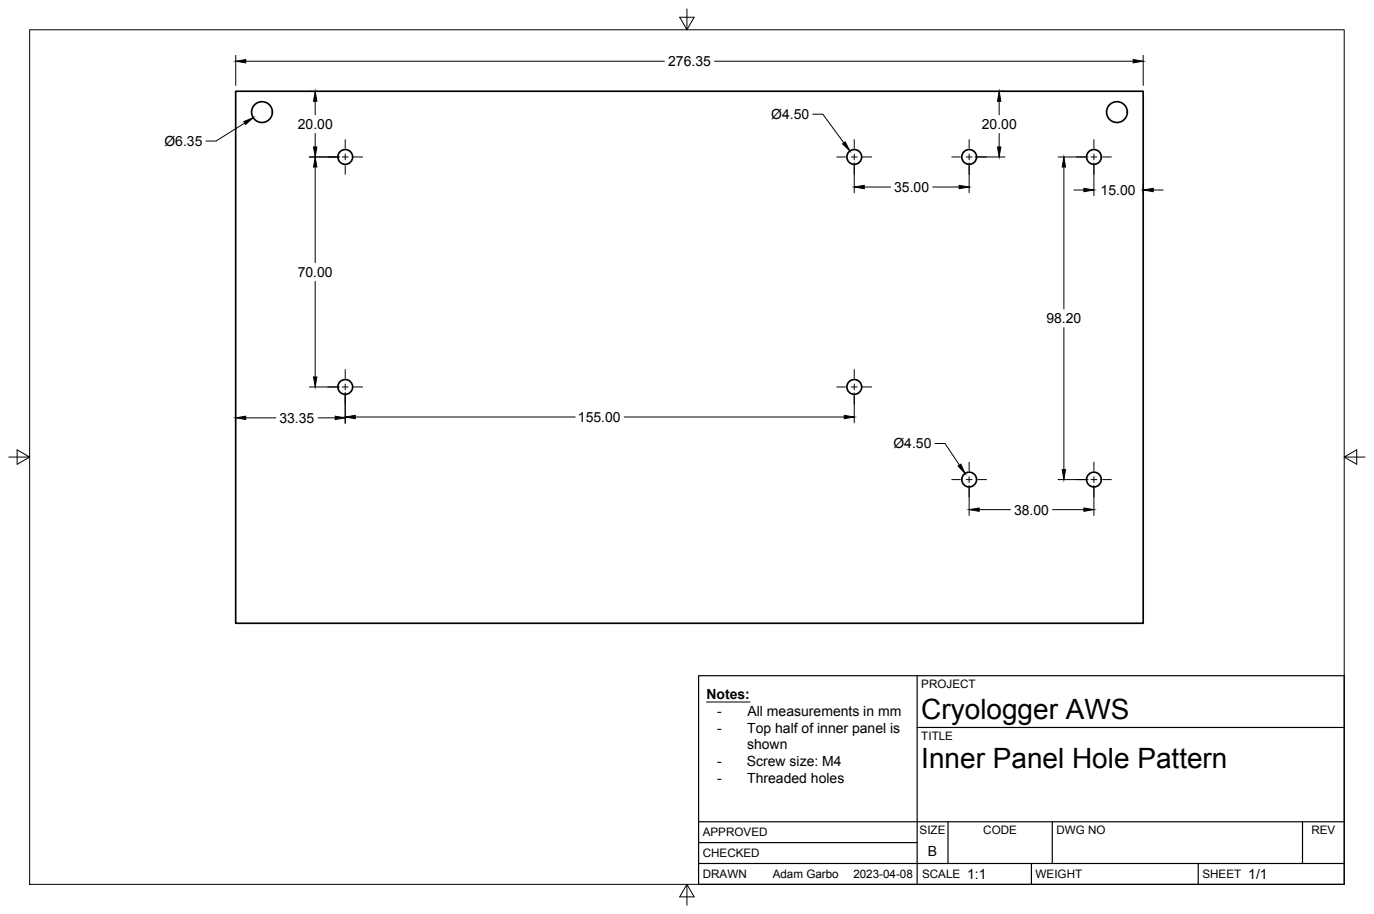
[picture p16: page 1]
SIZE; CODE; DWG NO; REV; Adam Garbo

PROJECT
Cryologger AWS
Inner Panel Hole Pattern

Notes:
- All measurements in mm
- Top half of inner panel is
shown
- Screw size: M4
- Threaded holes

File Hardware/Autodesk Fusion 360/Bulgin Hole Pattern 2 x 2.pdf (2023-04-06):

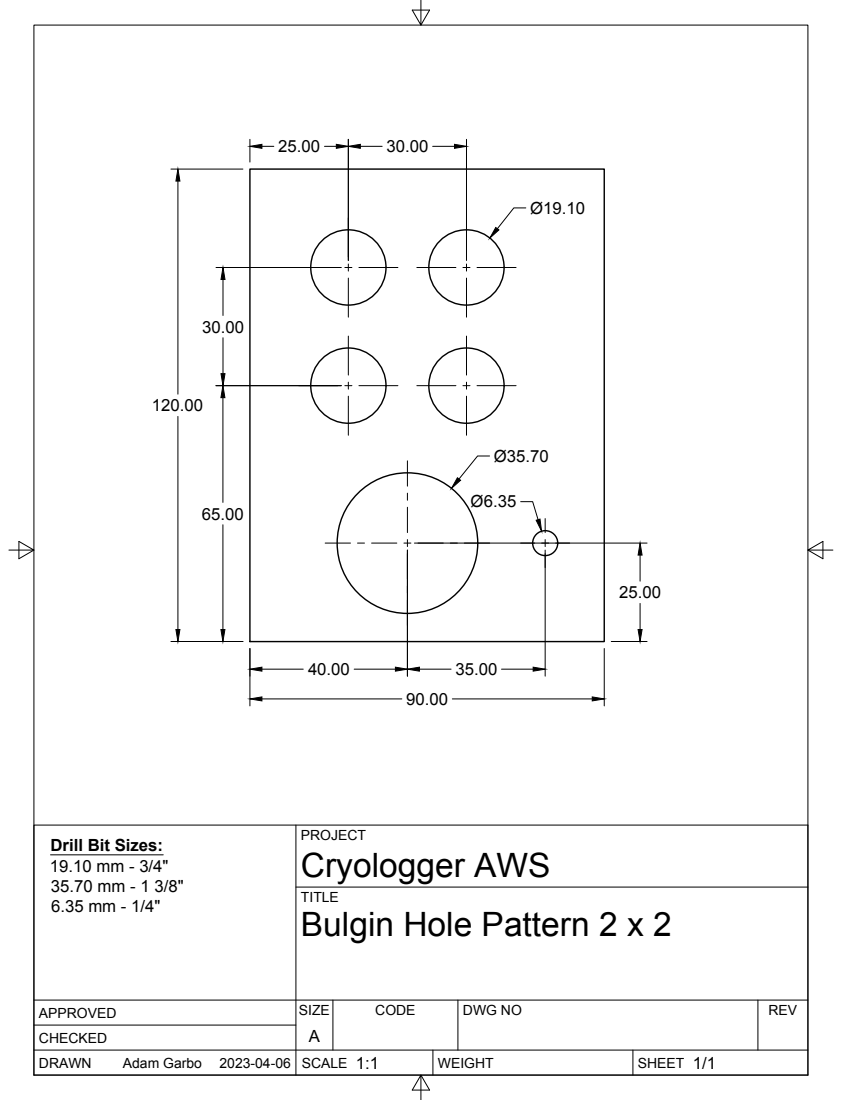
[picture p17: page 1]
SIZE; CODE; DWG NO; REV; Adam Garbo

Drill Bit Sizes:

PROJECT
Cryologger AWS
Bulgin Hole Pattern 2 x 2

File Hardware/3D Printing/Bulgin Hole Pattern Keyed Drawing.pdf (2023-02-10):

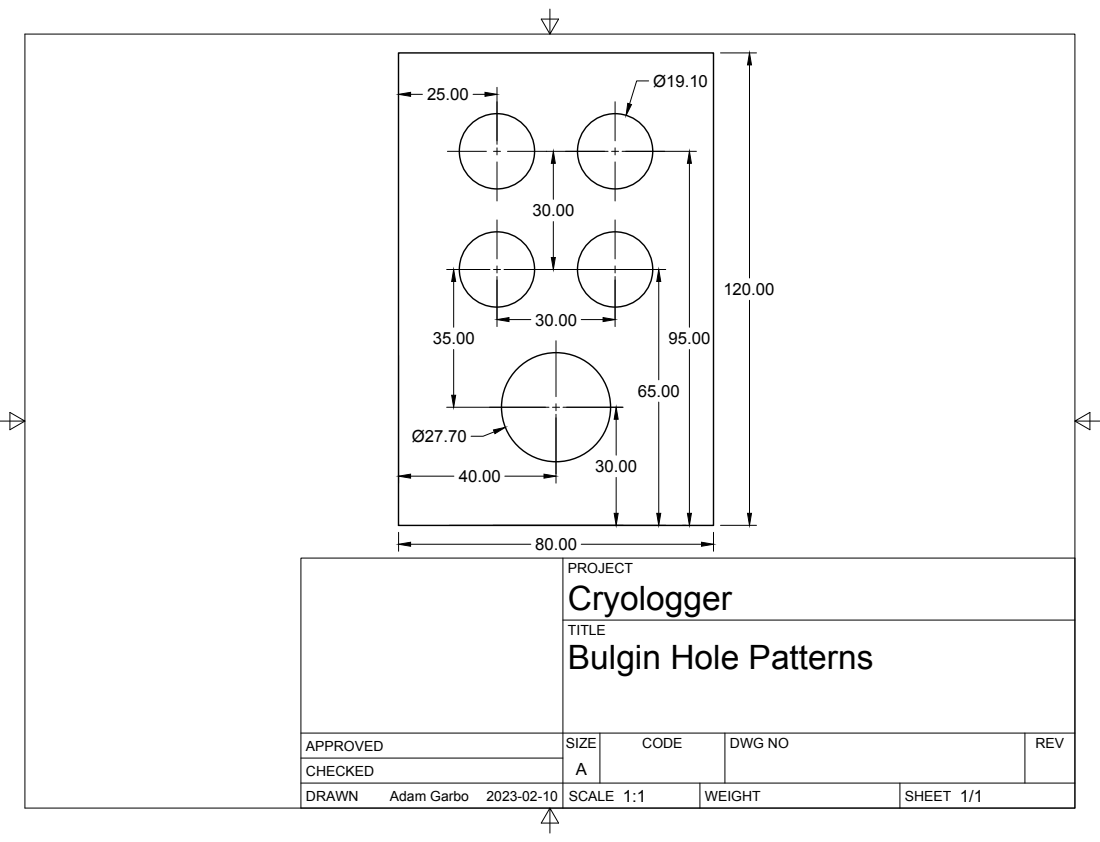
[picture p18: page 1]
SIZE; CODE; DWG NO; REV; Adam Garbo; Bulgin Hole Patterns

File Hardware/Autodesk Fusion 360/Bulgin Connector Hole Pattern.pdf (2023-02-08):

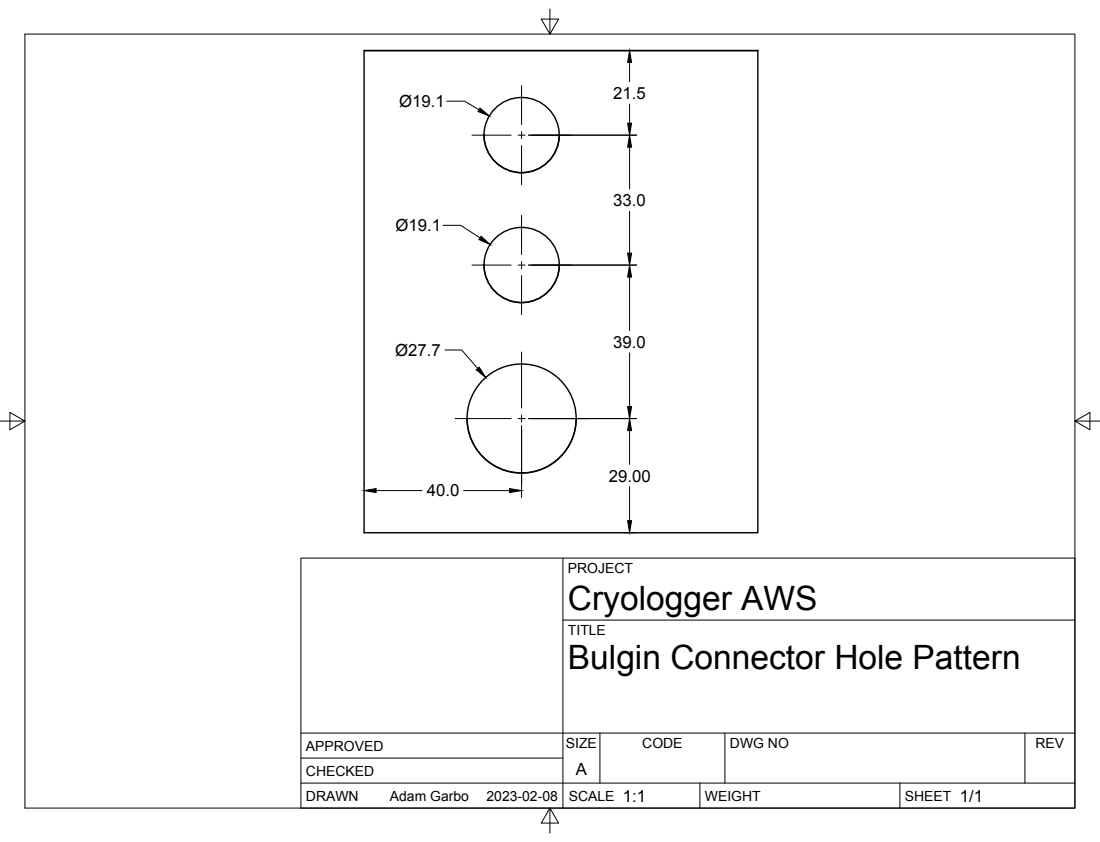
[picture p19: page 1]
SIZE; CODE; DWG NO; REV; Adam Garbo

PROJECT
Cryologger AWS
Bulgin Connector Hole Pattern

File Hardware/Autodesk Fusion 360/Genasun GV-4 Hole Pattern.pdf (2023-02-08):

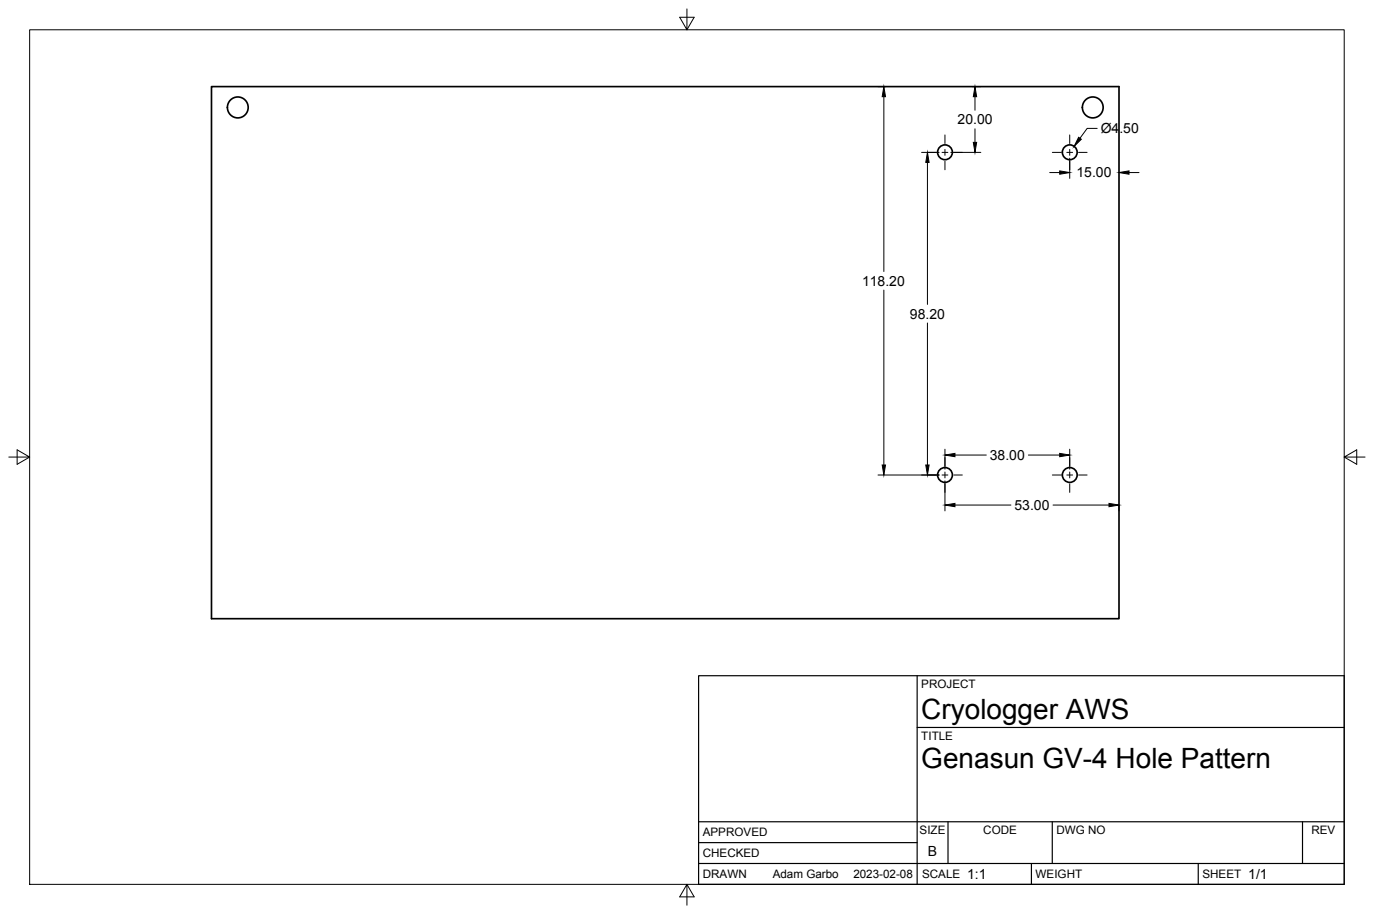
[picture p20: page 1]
SIZE; CODE; DWG NO; REV; Adam Garbo

PROJECT
Cryologger AWS
Genasun GV-4 Hole Pattern

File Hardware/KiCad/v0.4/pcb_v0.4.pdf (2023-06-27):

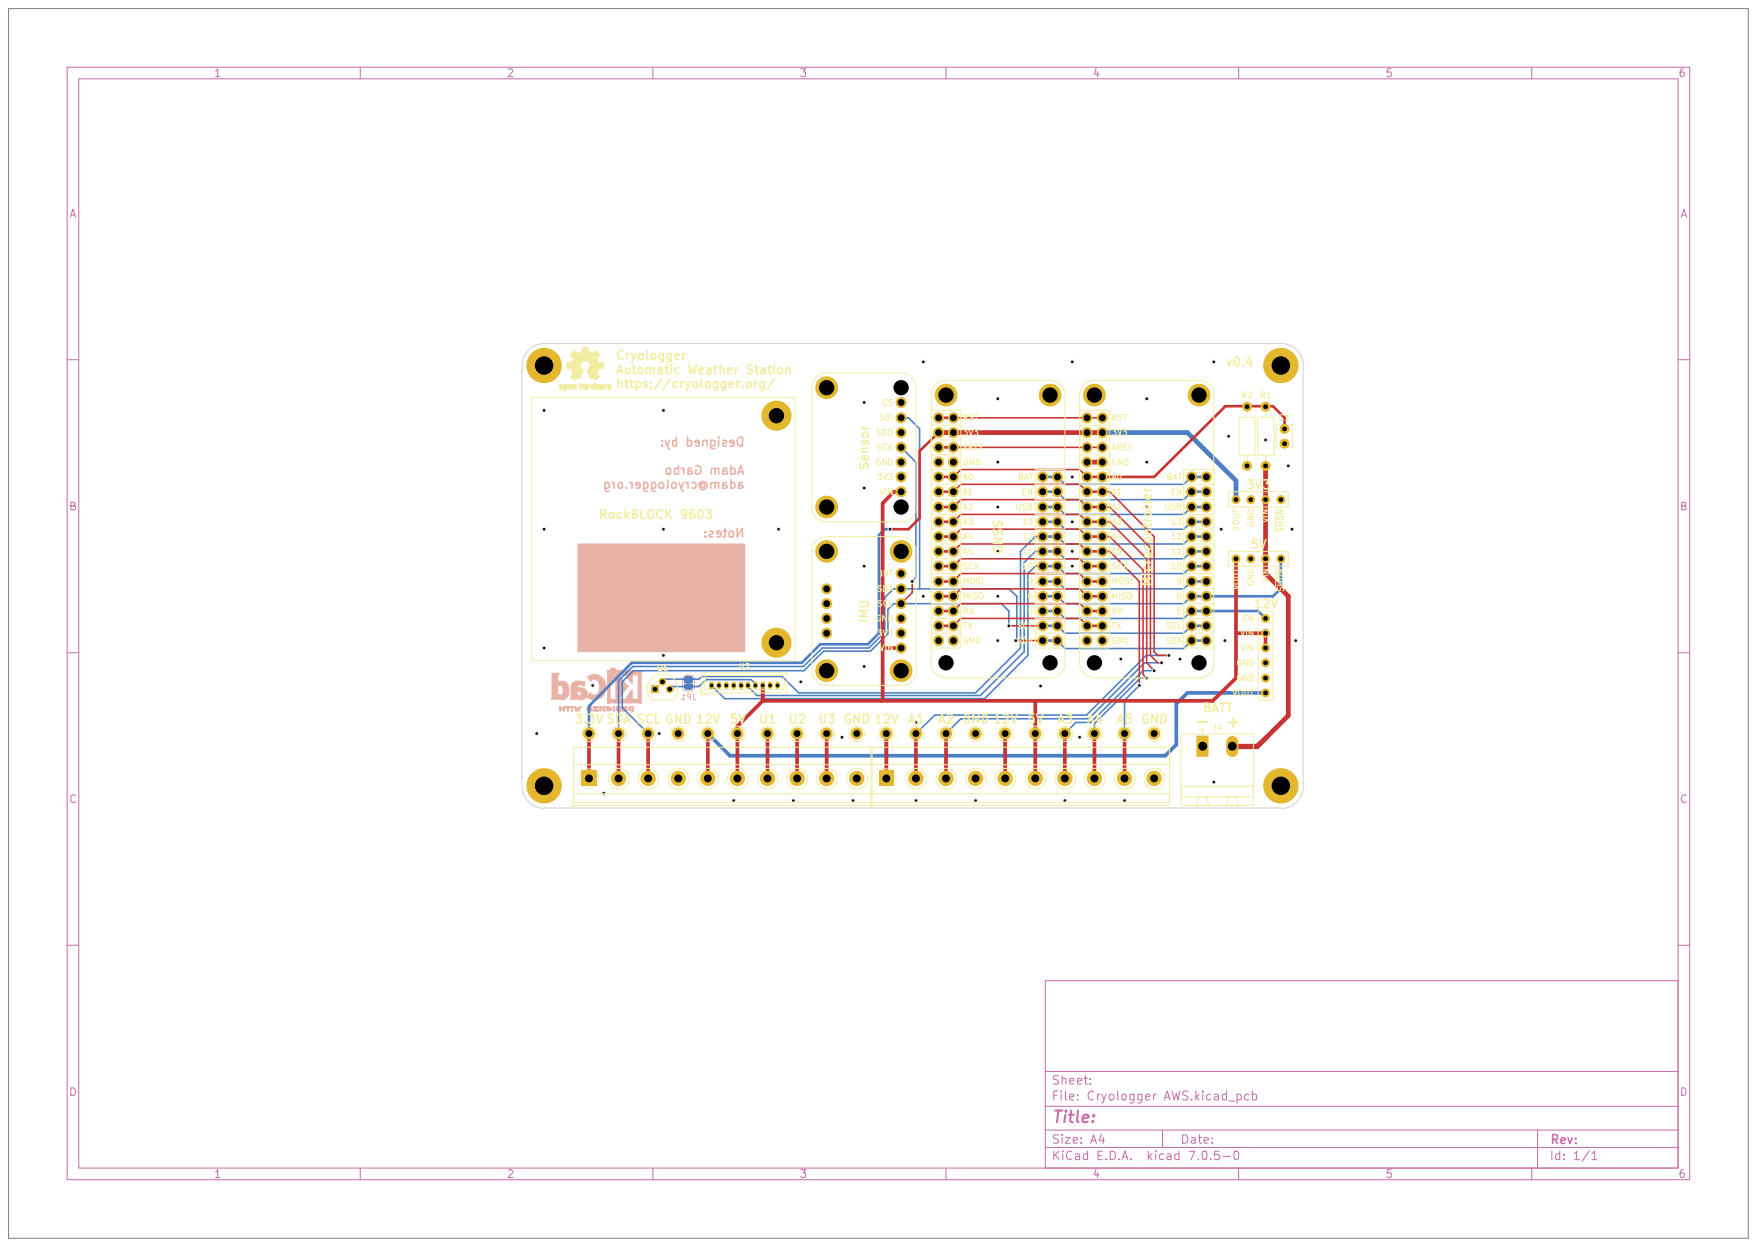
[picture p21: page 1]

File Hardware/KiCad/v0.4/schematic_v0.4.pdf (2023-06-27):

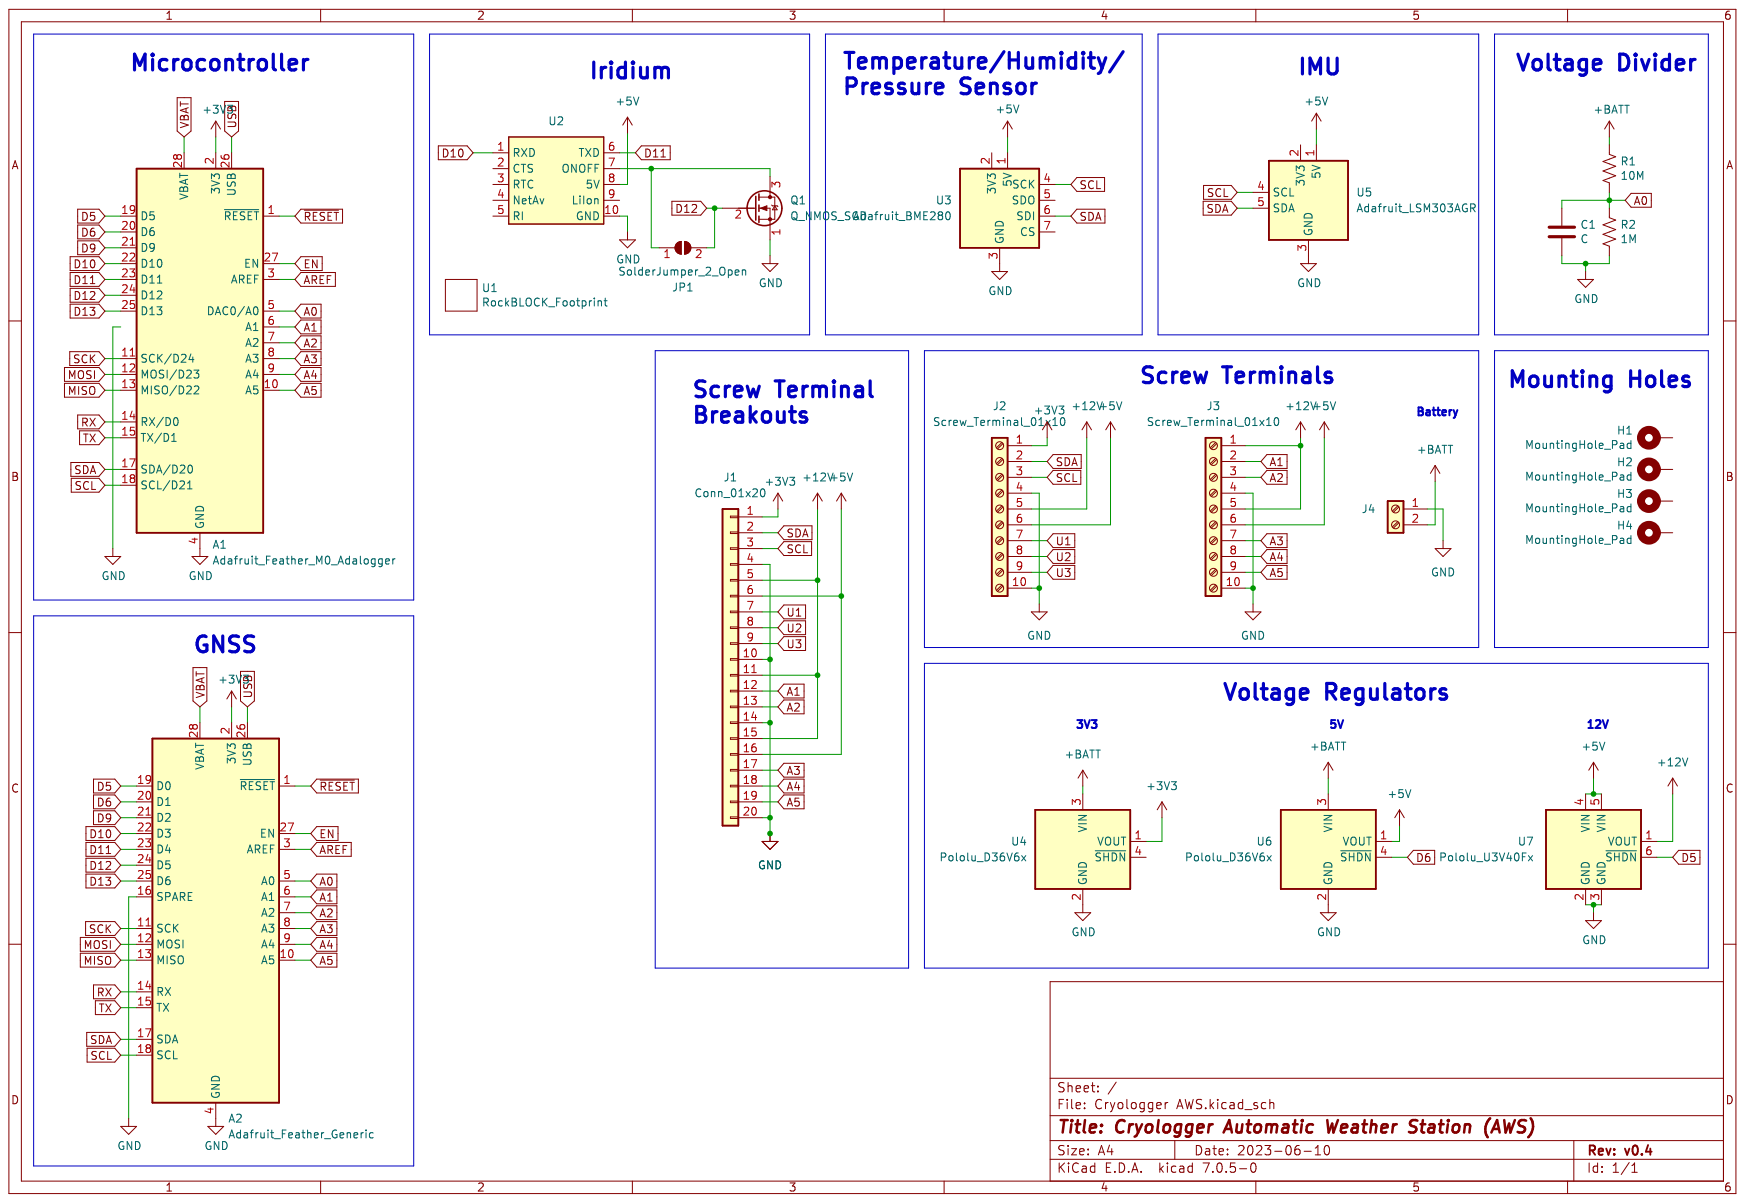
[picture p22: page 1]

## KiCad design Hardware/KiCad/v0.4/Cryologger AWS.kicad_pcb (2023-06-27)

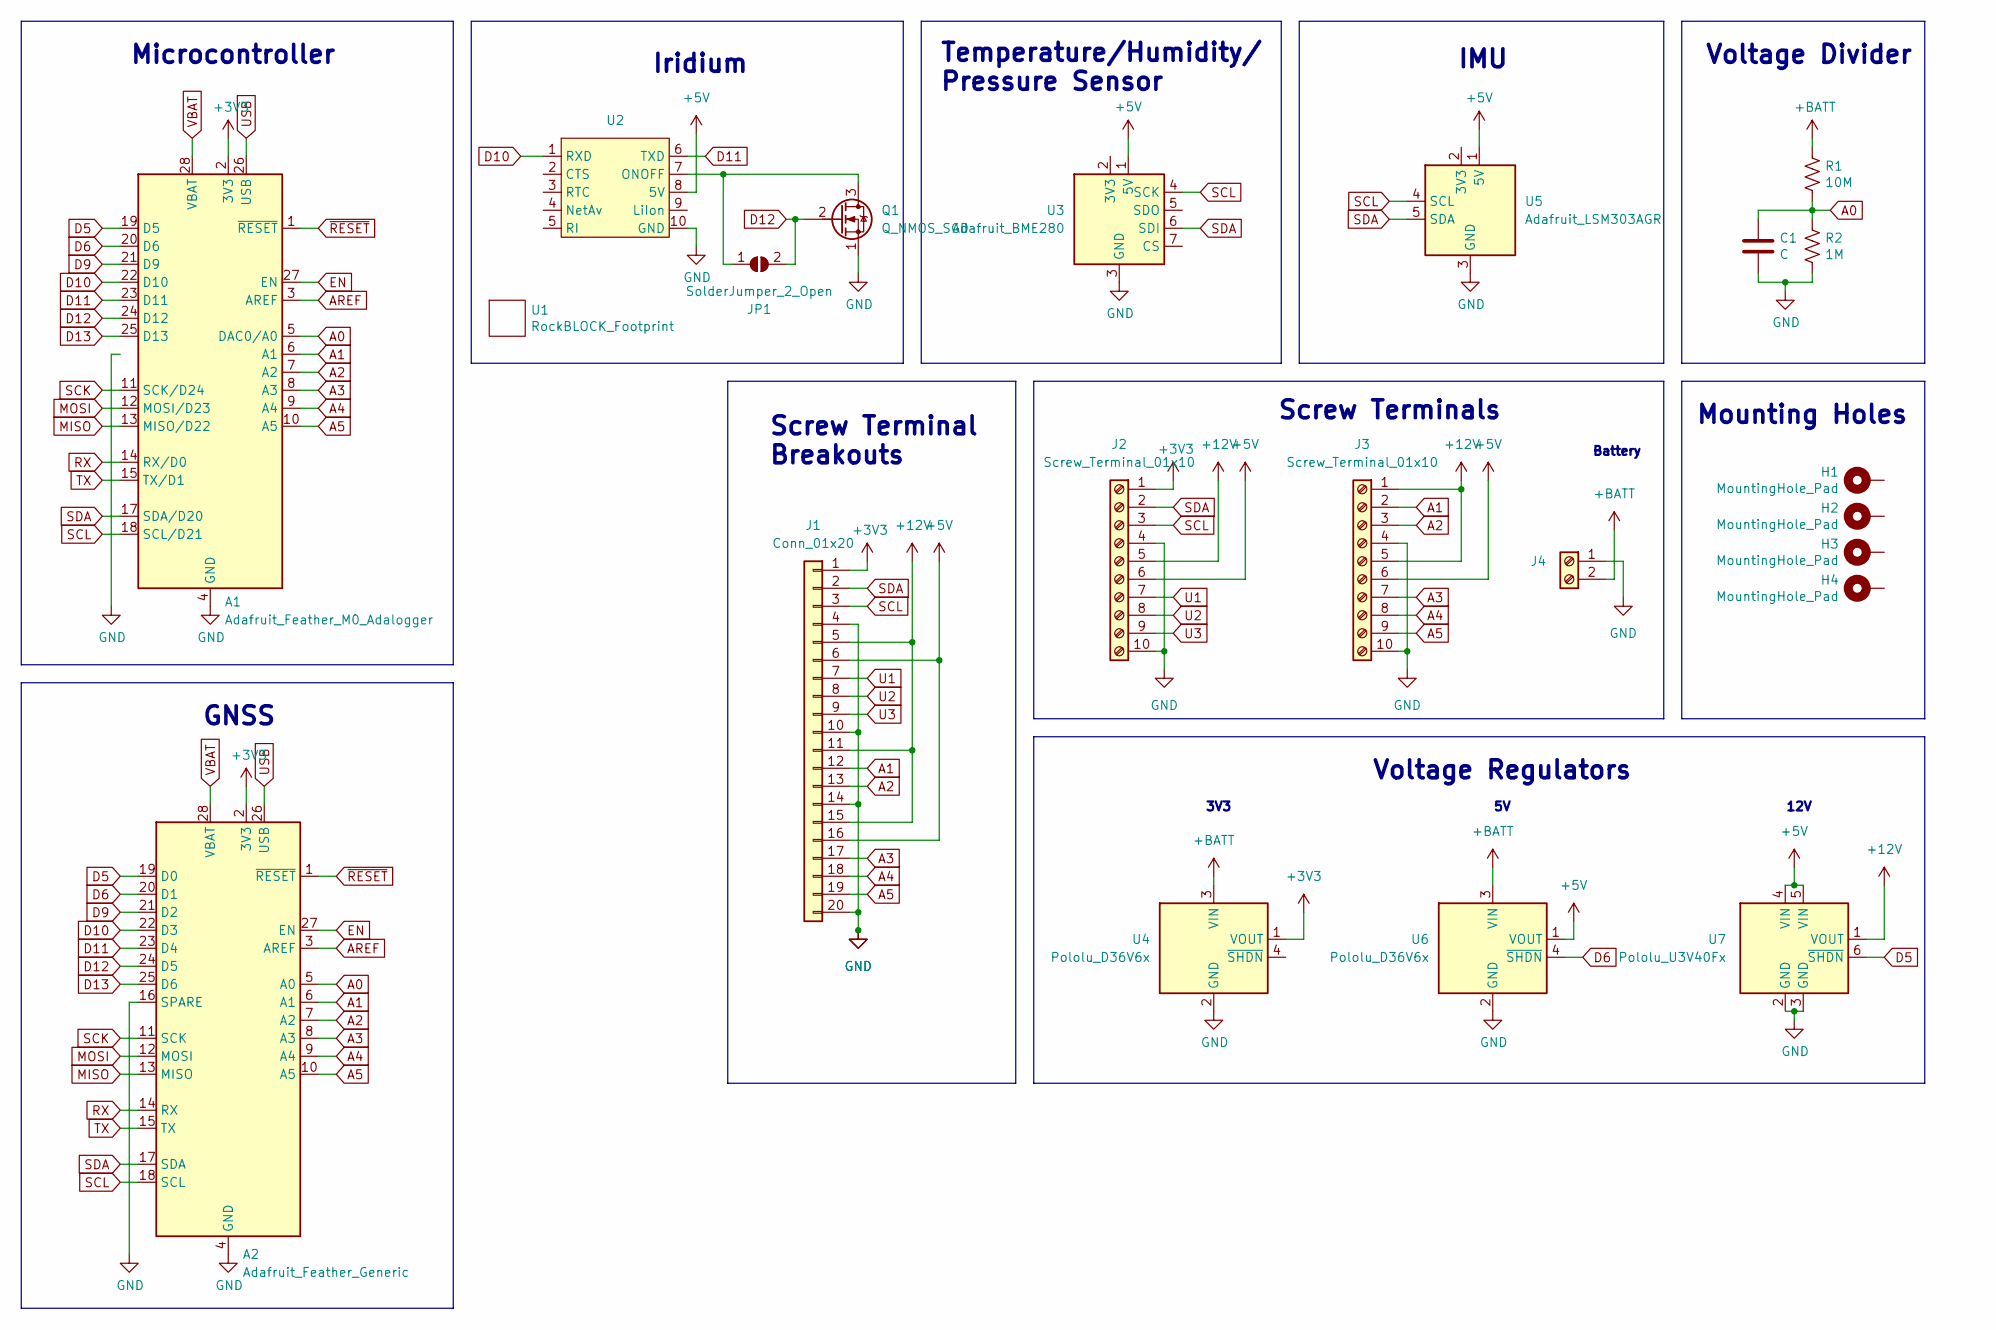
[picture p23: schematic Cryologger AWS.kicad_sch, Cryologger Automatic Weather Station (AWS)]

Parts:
A1: Adafruit_Feather_M0_Adalogger; Adafruit_Feather_Header_Double
A2: Adafruit_Feather_Generic; Adafruit_Feather_Header_Double
C1: C; C_Disc_D3.8mm_W2.6mm_P2.50mm
H1, H2, H3, H4: MountingHole_Pad; MountingHole_3mm_Pad
J1: Conn_01x20; Pin_1.0mm_10.0mm_1x20
J2, J3: Screw_Terminal_01x10; TerminalBlock_Phoenix_MKDS-1,5-10-5.08_1x10_P5.08mm_Horizon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
J4: Screw_Terminal_01x02; PhoenixContact_MSTBA_2,5_2-G-5,08_1x02_P5.08mm_Horizontal
JP1: SolderJumper_2_Open; SolderJumper-2_P1.3mm_Open_RoundedPad1.0x1.5mm
Q1: Q_NMOS_SGD; TO-92
R1: 10M; R_Axial_DIN0207_L6.3mm_D2.5mm_P10.16mm_Horizontal
R2: 1M; R_Axial_DIN0207_L6.3mm_D2.5mm_P10.16mm_Horizontal
U1: RockBLOCK_Footprint; RockBLOCK_9603
U2: Molex_PicoBlade_53047-1010_1x10_P1.25mm_Vertical
U3: Adafruit_BME280
U4, U6: Pololu_D36V6x
U5: Adafruit_LSM303AGR
U7: Pololu_U3V40Fx

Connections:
+3V3: A1.2 (3V3), A2.2 (3V3), J1.1, J2.1, U4.1 (VOUT)
+5V: J1.6, J1.16, J2.6, J3.6, U2.8 (5V), U3.1 (5V), U5.1 (5V), U6.1 (VOUT), U7.4 (VIN), U7.5 (VIN)
+12V: J1.5, J1.11, J1.15, J2.5, J3.1, J3.5, U7.1 (VOUT)
+BATT: J4.2, R1.1, U4.3 (VIN), U6.3 (VIN)
A0: A1.5 (DAC0/A0), A2.5 (A0), C1.1, R1.2, R2.1
A1: A1.6 (A1), A2.6 (A1), J1.12, J3.2
A2: A1.7 (A2), A2.7 (A2), J1.13, J3.3
A3: A1.8 (A3), A2.8 (A3), J1.17, J3.7
A4: A1.9 (A4), A2.9 (A4), J1.18, J3.8
A5: A1.10 (A5), A2.10 (A5), J1.19, J3.9
AREF: A1.3 (AREF), A2.3 (AREF)
D5: A1.19 (D5), A2.19 (D0), U7.6 (~SHDN)
D6: A1.20 (D6), A2.20 (D1), U6.4 (~SHDN)
D9: A1.21 (D9), A2.21 (D2)
D10: A1.22 (D10), A2.22 (D3), U2.1 (RXD)
D11: A1.23 (D11), A2.23 (D4), U2.6 (TXD)
D12: A1.24 (D12), A2.24 (D5), JP1.2 (B), Q1.2 (G)
D13: A1.25 (D13), A2.25 (D6)
EN: A1.27 (EN), A2.27 (EN)
GND: A1.4 (GND), A1.16 (GND), A2.4 (GND), A2.16 (SPARE), C1.2, J1.4, J1.10, J1.14, J1.20, J2.4, J2.10, J3.4, J3.10, J4.1, Q1.1 (S), R2.2, U2.10 (GND), U3.3 (GND), U4.2 (GND), U5.3 (GND), U6.2 (GND), U7.2 (GND), U7.3 (GND)
MISO: A1.13 (MISO/D22), A2.13 (MISO)
MOSI: A1.12 (MOSI/D23), A2.12 (MOSI)
unnamed: JP1.1 (A), Q1.3 (D), U2.7 (ONOFF)
RX: A1.14 (RX/D0), A2.14 (RX)
SCK: A1.11 (SCK/D24), A2.11 (SCK)
SCL: A1.18 (SCL/D21), A2.18 (SCL), J1.3, J2.3, U3.4 (SCK), U5.4 (SCL)
SDA: A1.17 (SDA/D20), A2.17 (SDA), J1.2, J2.2, U3.6 (SDI), U5.5 (SDA)
TX: A1.15 (TX/D1), A2.15 (TX)
U1: J1.7, J2.7
U2: J1.8, J2.8
U3: J1.9, J2.9
USB: A1.26 (USB), A2.26 (USB)
VBAT: A1.28 (VBAT), A2.28 (VBAT)
~RESET: A1.1 (~RESET), A2.1 (~RESET)

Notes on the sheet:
Screw Terminals
Iridium
Voltage Regulators
Voltage Divider
GNSS
IMU
Microcontroller
Screw Terminal Breakouts
3V3
Battery
Temperature/Humidity/ Pressure Sensor
12V
Mounting Holes

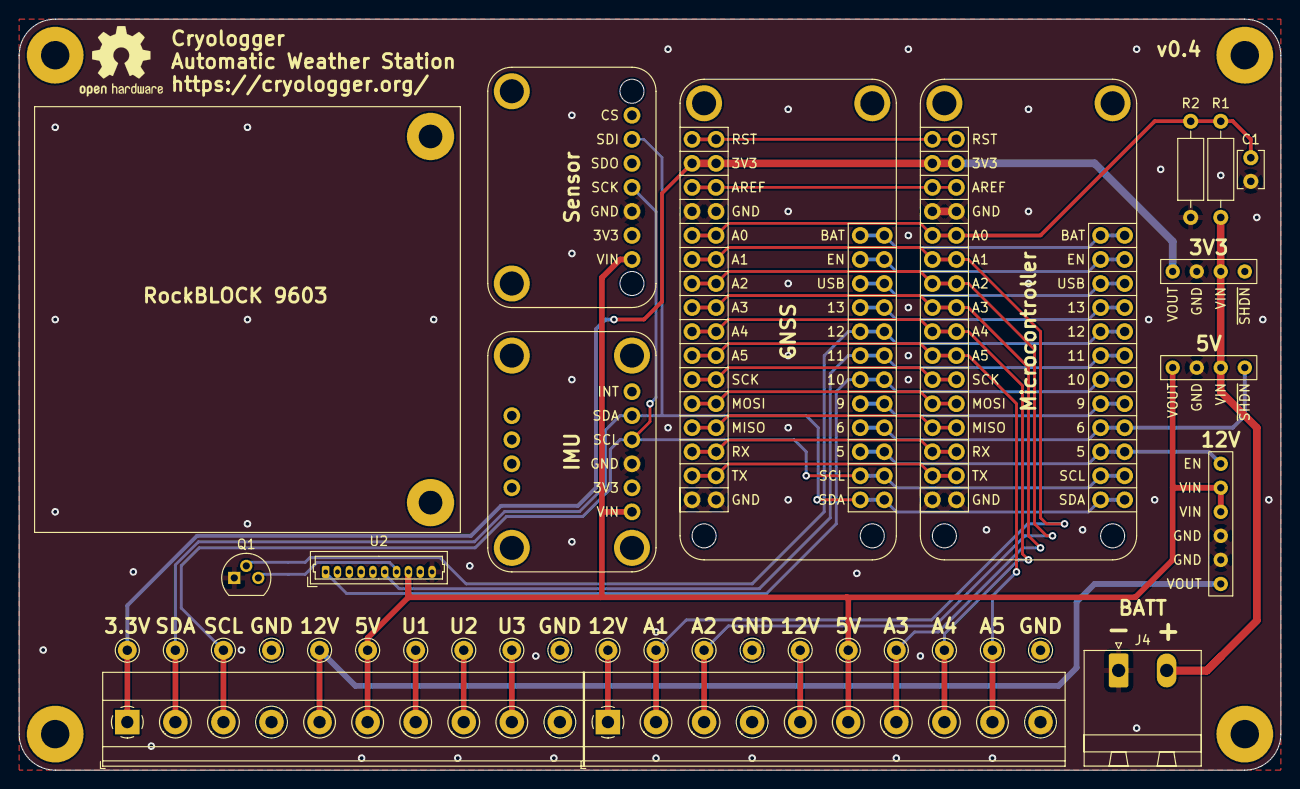
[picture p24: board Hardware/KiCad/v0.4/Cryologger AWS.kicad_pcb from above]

Board: 2 copper layers, 133.3 x 79.4 mm, 22 parts (1 on the bottom side), 34 nets.

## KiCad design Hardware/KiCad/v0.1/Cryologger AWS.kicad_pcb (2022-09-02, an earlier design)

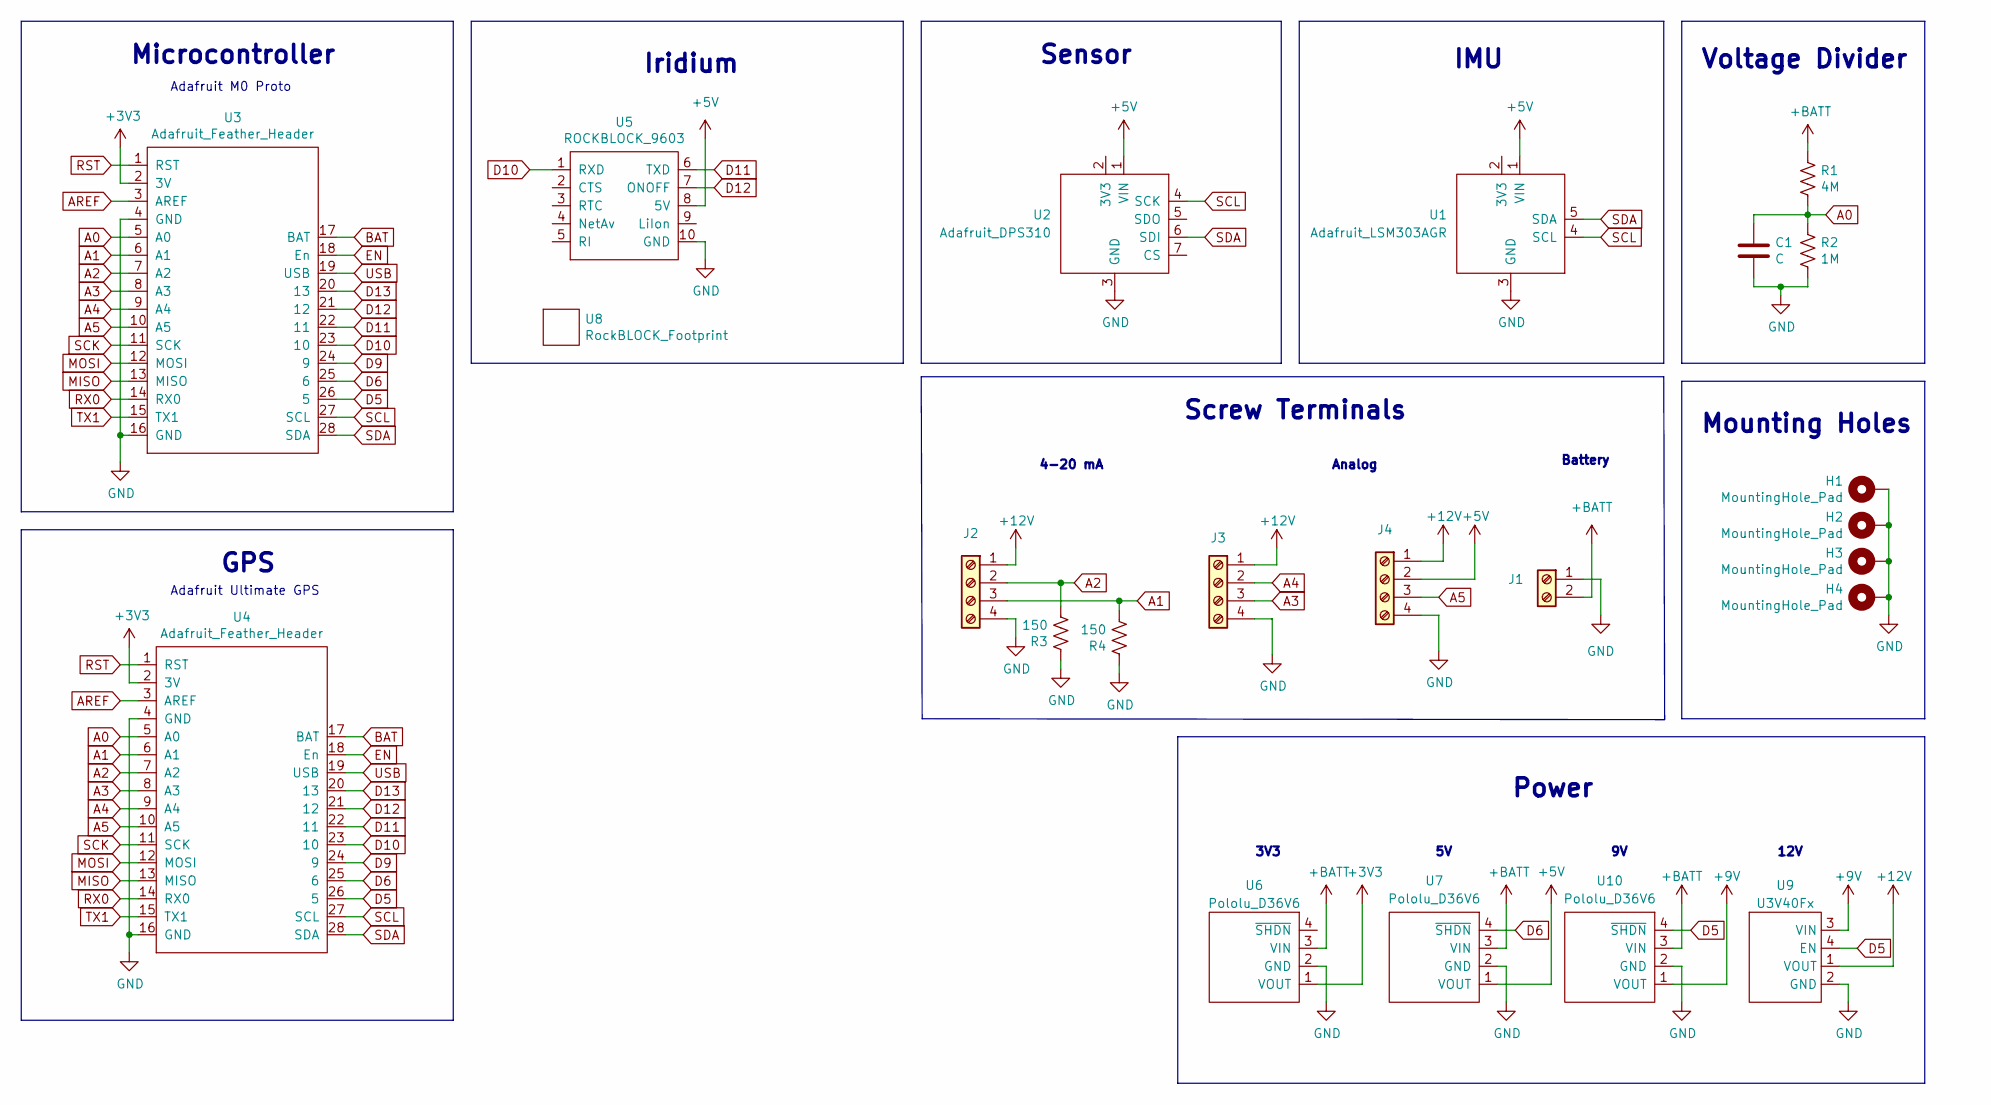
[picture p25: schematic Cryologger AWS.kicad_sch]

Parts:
C1: C; C_Disc_D3.8mm_W2.6mm_P2.50mm
H1, H2, H3, H4: MountingHole_Pad; MountingHole_3mm_Pad
J1: Screw_Terminal_01x02; PhoenixContact_MSTBA_2,5_2-G-5,08_1x02_P5.08mm_Horizontal
J2, J3, J4: Screw_Terminal_01x04; PhoenixContact_MSTBA_2,5_4-G-5,08_1x04_P5.08mm_Horizontal
R1: 4M; R_Axial_DIN0207_L6.3mm_D2.5mm_P10.16mm_Horizontal
R2: 1M; R_Axial_DIN0207_L6.3mm_D2.5mm_P10.16mm_Horizontal
R3, R4: 150; R_Axial_DIN0207_L6.3mm_D2.5mm_P10.16mm_Horizontal
U1: Adafruit_LSM303AGR
U2: Adafruit_DPS310
U3, U4: Adafruit_Feather_Header; Adafruit_Feather_Header_Double
U5: ROCKBLOCK_9603; Molex_PicoBlade_53047-1010_1x10_P1.25mm_Vertical
U6, U7, U10: Pololu_D36V6; Pololu D36V6x
U8: RockBLOCK_Footprint; RockBLOCK_9603_Footprint
U9: U3V40Fx; Pololu U3V40Fx

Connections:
+3V3: U3.2 (3V), U4.2 (3V), U6.1 (VOUT)
+5V: J4.2, U1.1 (VIN), U2.1 (VIN), U5.8 (5V), U7.1 (VOUT)
+9V: U9.3 (VIN), U10.1 (VOUT)
+12V: J2.1, J3.1, J4.1, U9.1 (VOUT)
+BATT: J1.2, R1.1, U6.3 (VIN), U7.3 (VIN), U10.3 (VIN)
A0: C1.1, R1.2, R2.1, U3.5 (A0), U4.5 (A0)
A1: J2.3, R4.2, U3.6 (A1), U4.6 (A1)
A2: J2.2, R3.2, U3.7 (A2), U4.7 (A2)
A3: J3.3, U3.8 (A3), U4.8 (A3)
A4: J3.2, U3.9 (A4), U4.9 (A4)
A5: J4.3, U3.10 (A5), U4.10 (A5)
AREF: U3.3 (AREF), U4.3 (AREF)
BAT: U3.17 (BAT), U4.17 (BAT)
D5: U3.26 (5), U4.26 (5), U9.4 (EN), U10.4 (~SHDN)
D6: U3.25 (6), U4.25 (6), U7.4 (~SHDN)
D9: U3.24 (9), U4.24 (9)
D10: U3.23 (10), U4.23 (10), U5.1 (RXD)
D11: U3.22 (11), U4.22 (11), U5.6 (TXD)
D12: U3.21 (12), U4.21 (12), U5.7 (ONOFF)
D13: U3.20 (13), U4.20 (13)
EN: U3.18 (En), U4.18 (En)
GND: C1.2, H1.1, H2.1, H3.1, H4.1, J1.1, J2.4, J3.4, J4.4, R2.2, R3.1, R4.1, U1.3 (GND), U2.3 (GND), U3.4 (GND), U3.16 (GND), U4.4 (GND), U4.16 (GND), U5.10 (GND), U6.2 (GND), U7.2 (GND), U9.2 (GND), U10.2 (GND)
MISO: U3.13 (MISO), U4.13 (MISO)
MOSI: U3.12 (MOSI), U4.12 (MOSI)
RST: U3.1 (RST), U4.1 (RST)
RX0: U3.14 (RX0), U4.14 (RX0)
SCK: U3.11 (SCK), U4.11 (SCK)
SCL: U1.4 (SCL), U2.4 (SCK), U3.27 (SCL), U4.27 (SCL)
SDA: U1.5 (SDA), U2.6 (SDI), U3.28 (SDA), U4.28 (SDA)
TX1: U3.15 (TX1), U4.15 (TX1)
USB: U3.19 (USB), U4.19 (USB)

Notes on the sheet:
Screw Terminals
Iridium
Power
Voltage Divider
IMU
Microcontroller
Adafruit Ultimate GPS
3V3
Adafruit M0 Proto
4-20 mA
Battery
Analog
Sensor
GPS
12V
Mounting Holes

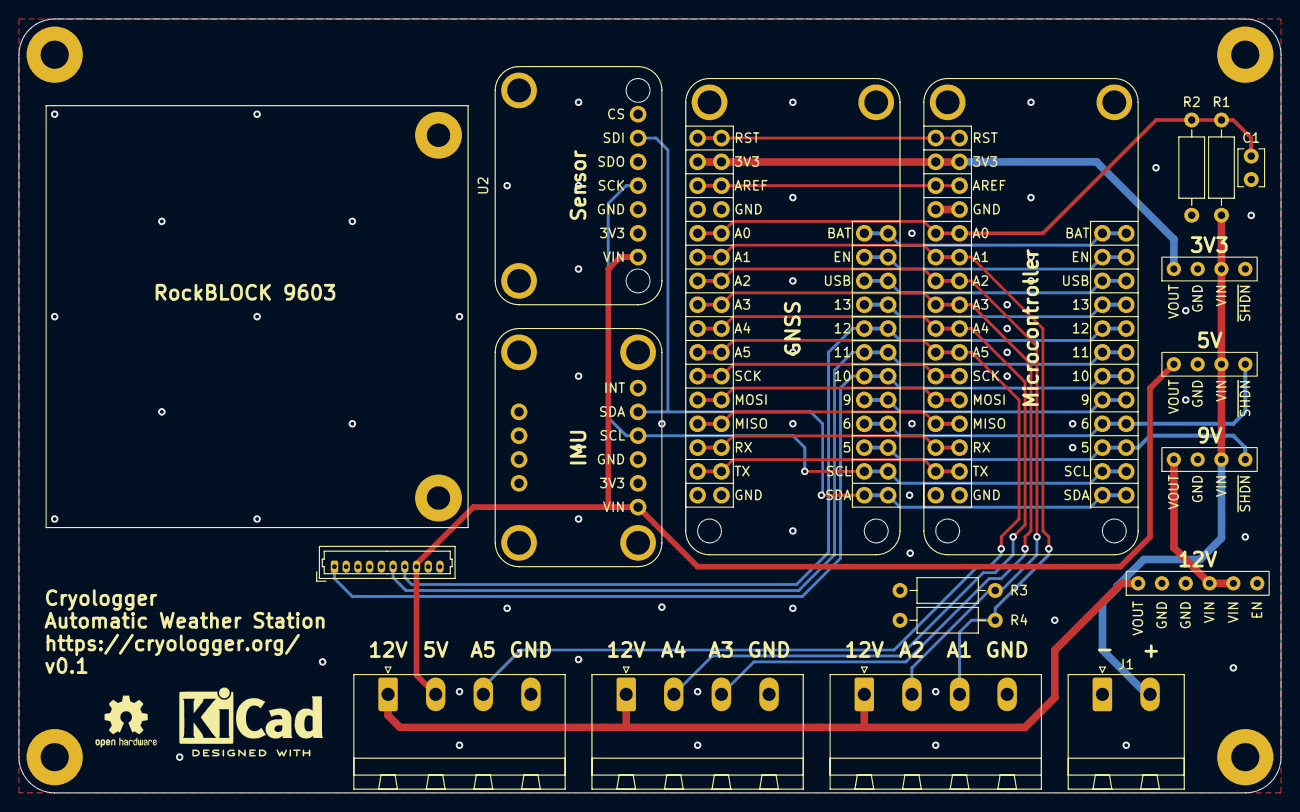
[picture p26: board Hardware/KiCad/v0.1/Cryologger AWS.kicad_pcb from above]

Board: 2 copper layers, 134.6 x 82.5 mm, 23 parts (0 on the bottom side), 31 nets.

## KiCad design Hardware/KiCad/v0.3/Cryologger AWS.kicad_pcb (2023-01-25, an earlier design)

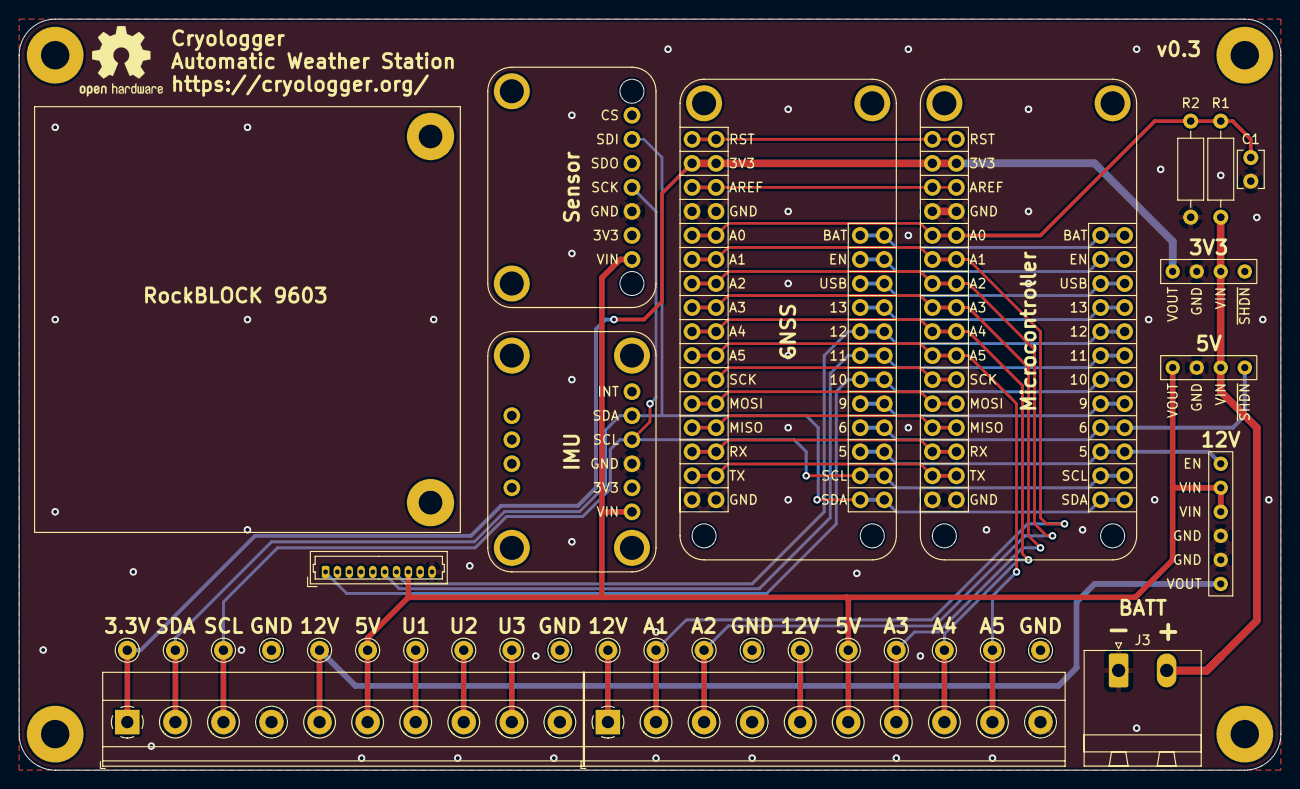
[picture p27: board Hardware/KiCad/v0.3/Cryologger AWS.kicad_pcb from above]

Board: 2 copper layers, 133.3 x 79.4 mm, 20 parts (0 on the bottom side), 33 nets.

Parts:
C1: C; C_Disc_D3.8mm_W2.6mm_P2.50mm
H1, H2, H3, H4: MountingHole_Pad; MountingHole_3mm_Pad
J1, J2: Screw_Terminal_01x10; TerminalBlock_Phoenix_MKDS-1,5-10-5.08_1x10_P5.08mm_Horizon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
J3: Screw_Terminal_01x02; PhoenixContact_MSTBA_2,5_2-G-5,08_1x02_P5.08mm_Horizontal
J4: Conn_01x20; Pin_1.0mm_10.0mm_1x20
R1: 4M; R_Axial_DIN0207_L6.3mm_D2.5mm_P10.16mm_Horizontal
R2: 1M; R_Axial_DIN0207_L6.3mm_D2.5mm_P10.16mm_Horizontal
U1, U2: Adafruit_Feather_Header; Adafruit_Feather_Header_Double
U3: RockBLOCK_Footprint; RockBLOCK_9603
U4: ROCKBLOCK_9603; Molex_PicoBlade_53047-1010_1x10_P1.25mm_Vertical
U5: Adafruit_DPS310
U6, U7: Pololu_D36V6x
U8: Adafruit_LSM303AGR
U9: Pololu_U3V40Fx

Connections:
+3V3: J1.1, J4.1, U1.2 (3V), U2.2 (3V), U6.1 (VOUT)
+5V: J1.6, J2.6, J4.6, J4.16, U4.8 (5V), U5.1 (5V), U7.1 (VOUT), U8.1 (5V), U9.3 (VIN)
+12V: J1.5, J2.1, J2.5, J4.5, J4.11, J4.15, U9.1 (VOUT)
+BATT: J3.2, R1.1, U6.3 (VIN), U7.3 (VIN)
A0: C1.1, R1.2, R2.1, U1.5 (A0), U2.5 (A0)
A1: J2.2, J4.12, U1.6 (A1), U2.6 (A1)
A2: J2.3, J4.13, U1.7 (A2), U2.7 (A2)
A3: J2.7, J4.17, U1.8 (A3), U2.8 (A3)
A4: J2.8, J4.18, U1.9 (A4), U2.9 (A4)
A5: J2.9, J4.19, U1.10 (A5), U2.10 (A5)
AREF: U1.3 (AREF), U2.3 (AREF)
BAT: U1.17 (BAT), U2.17 (BAT)
D5: U1.26 (5), U2.26 (5), U9.4 (EN)
D6: U1.25 (6), U2.25 (6), U7.4 (~{SHDN)
D9: U1.24 (9), U2.24 (9)
D10: U1.23 (10), U2.23 (10), U4.1 (RXD)
D11: U1.22 (11), U2.22 (11), U4.6 (TXD)
D12: U1.21 (12), U2.21 (12), U4.7 (ONOFF)
D13: U1.20 (13), U2.20 (13)
EN: U1.18 (En), U2.18 (En)
GND: C1.2, J1.4, J1.10, J2.4, J2.10, J3.1, J4.4, J4.10, J4.14, J4.20, R2.2, U1.4 (GND), U1.16 (GND), U2.4 (GND), U2.16 (GND), U4.10 (GND), U5.3 (GND), U6.2 (GND), U7.2 (GND), U8.3 (GND), U9.2 (GND)
MISO: U1.13 (MISO), U2.13 (MISO)
MOSI: U1.12 (MOSI), U2.12 (MOSI)
RST: U1.1 (RST), U2.1 (RST)
RX0: U1.14 (RX0), U2.14 (RX0)
SCK: U1.11 (SCK), U2.11 (SCK)
SCL: J1.3, J4.3, U1.27 (SCL), U2.27 (SCL), U5.4 (SCK), U8.4 (SCL)
SDA: J1.2, J4.2, U1.28 (SDA), U2.28 (SDA), U5.6 (SDI), U8.5 (SDA)
TX1: U1.15 (TX1), U2.15 (TX1)
U1: J1.7, J4.7
U2: J1.8, J4.8
U3: J1.9, J4.9
USB: U1.19 (USB), U2.19 (USB)

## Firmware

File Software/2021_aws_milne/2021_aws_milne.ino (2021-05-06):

/*
  Title:    Cryologger Automatic Weather Station (AWS)
  Date:     May 6, 2021
  Author:   Adam Garbo

  Components:
  - Adafruit Feather M0 Adalogger
  - Adafruit DS3231 RTC Precision Featherwing
  - Davis Instruments 7911 Anemomenter
  - Davis Instruments 6830 Temperature/Relative Humidity
  - Rock Seven RockBLOCK 9603
  - 256 MB microSD card (Industrial rated)

  Comments:
  - Automatic weather station to be deployed in the summer of 2021 on Ellesmere Island.
*/

// ------------------------------------------------------------------------------------------------
// Libraries
// ------------------------------------------------------------------------------------------------
#include <Arduino.h>                // Must be included before wiring_private.h
#include <ArduinoLowPower.h>        // https://github.com/arduino-libraries/ArduinoLowPower
#include <DS3232RTC.h>              // https://github.com/JChristensen/DS3232RTC
#include <IridiumSBD.h>             // https://github.com/mikalhart/IridiumSBD
#include <math.h>                   // https://www.nongnu.org/avr-libc/user-manual/group__avr__math.html
#include <SAMD_AnalogCorrection.h>  // https://github.com/arduino/ArduinoCore-samd/tree/master/libraries/SAMD_AnalogCorrection
#include <sensirion.h>              // https://github.com/HydroSense/sensirion
#include <Statistic.h>              // https://github.com/RobTillaart/Statistic
#include <SdFat.h>                  // https://github.com/greiman/SdFat
#include <TinyGPS++.h>              // https://github.com/mikalhart/TinyGPSPlus
#include <SPI.h>                    // https://www.arduino.cc/en/Reference/SPI
#include <Wire.h>                   // https://www.arduino.cc/en/Reference/Wire
#include <wiring_private.h>         // Required for creating new Serial instance with pinPeripheral() function 

// ------------------------------------------------------------------------------------------------
// Pin definitions
// ------------------------------------------------------------------------------------------------
#define PIN_RTC_INT           5
#define PIN_LED               8
#define PIN_IRIDIUM_EN        9
#define PIN_IRIDIUM_RX        10
#define PIN_IRIDIUM_TX        11
#define PIN_IRIDIUM_SLEEP     12
#define PIN_WIND_SPEED        A0
#define PIN_WIND_DIRECTION    A1
#define PIN_WIND_PWR          A2
#define PIN_TRH_PWR           A4
#define PIN_GPS_EN            A5
#define PIN_VBAT              A7

// Debugging constants
#define DEBUG         true    // Output debug messages to Serial Monitor
#define DEBUG_GPS     true    // Output GPS debug information
#define DEBUG_IRIDIUM true    // Output Iridium debug messages to Serial Monitor
#define DEPLOY        false   // Disable debugging messages for deployment

// ------------------------------------------------------------------------------------------------
// Port configuration
// ------------------------------------------------------------------------------------------------
// Create a new UART instance and assign it to pins 10 (RX) and 11 (TX).
// For more information see: https://www.arduino.cc/en/Tutorial/SamdSercom
Uart Serial2 (&sercom1, PIN_IRIDIUM_RX, PIN_IRIDIUM_TX, SERCOM_RX_PAD_2, UART_TX_PAD_0);

#define GPS_PORT      Serial1
#define IRIDIUM_PORT  Serial2

// Attach the interrupt handler to the SERCOM
void SERCOM1_Handler()
{
  Serial2.IrqHandler();
}

// ------------------------------------------------------------------------------------------------
// Object instantiations
// ------------------------------------------------------------------------------------------------
DS3232RTC       myRTC(false);             // Tell constructor not to initialize the I2C bus
IridiumSBD      modem(IRIDIUM_PORT, PIN_IRIDIUM_SLEEP);
SdFat           sd;                       // File system object
SdFile          file;                     // Log file
sensirion       sht(20, 21);              // sht(data pin, clock pin);

// ------------------------------------------------------------------------------------------------
// Statistic objects
// ------------------------------------------------------------------------------------------------
Statistic batteryStats;         // Battery voltage statistics
Statistic humidityStats;        // Humidity statistics
Statistic rtcStats;             // Real-time clock statistics
Statistic extTemperatureStats;  // External temperature statistics
Statistic windSpeedStats;       // Anemometer wind speed statistics
Statistic vnStats;              // Anemometer north-south wind vector component (v) statistics
Statistic veStats;              // Anemometer east-west wind vector component (u) statistics

// ------------------------------------------------------------------------------------------------
// User defined global variable declarations
// ------------------------------------------------------------------------------------------------
unsigned int          sampleInterval        = 60;          // Sleep duration (in seconds) between data sample acquisitions. Default = 5 minutes (300 seconds)
unsigned int          averageInterval       = 3;           // Number of samples to be averaged for each RockBLOCK transmission. Default = 12 (Hourly)
unsigned int          transmitInterval      = 100;          // Number of message to be included in a single transmission (340 byte limit). Default = 3 (Every 3 hours)
unsigned int          retransmitLimit       = 10;           // Maximum failed data transmissions to reattempt in a single message (340 byte limit). Default: 10
unsigned int          samplesPerFile        = 8640;         // Maximum samples stored in a file before new log file creation (Default: 30 days * 288 samples per day)

// ------------------------------------------------------------------------------------------------
// Global variable declarations
// ------------------------------------------------------------------------------------------------
const byte            chipSelect            = 4;            // MicroSD chip select pin
const byte            samplesToAverage      = 10;           // Number of samples to average
volatile bool         alarmFlag             = false;        // RTC interrupt service routine (ISR) flag
volatile bool         wdtFlag               = false;        // Watchdog Timer Early Warning interrupt flag
volatile byte         wdtCounter            = 0;            // Watchdog Timer trigger counter
volatile unsigned int revolutions           = 0;            // Wind speed 1 ISR revolutions counter
volatile unsigned int contactBounceTime     = 0;            // Anemometer debouncing variable
bool                  ledState              = LOW;          // Flag to toggle LED in blinkLed() function
bool                  logFlag               = true;         // MicroSD initilization flag
byte                  resetFlag             = 0;            // Watchdog Timer force reset flag
byte                  transmitBuffer[340]   = {};           // RockBLOCK transmission buffer
char                  fileName[12]          = "log000.csv"; // Log file naming convention
float                 humidity              = 0.0;          // SHT31 humidity (%)
float                 extTemperature        = 0.0;          // SHT31 temperature (°C)
float                 intTemperature        = 0.0;          // Internal RTC temperature (°C)
float                 voltage               = 0.0;          // Battery voltage in volts (V)
float                 windSpeed             = 0.0;          // Wind speed in metres per second (m/s)
float                 windGust              = 0.0;          // Wind gust speed in metres per second (m/s)
float                 windGustDirection     = 0.0;          // Wind gust direction in degrees (°)
unsigned int          windDirection         = 0;            // Wind direction in degrees (°)
unsigned int          samplePeriod          = 3;            // Wind speed sample period in seconds (s)
unsigned int          iterationCounter      = 0;            // Counter to track total number of program iterations (zero indicates a reset)
unsigned int          retransmitCounter     = 0;            // RockBLOCK failed data transmission counter
unsigned int          transmitCounter       = 0;            // RockBLOCK transmission interval counter
unsigned int          transmitDuration      = 0;            // RockBLOCK data transmission time variable
unsigned long         previousMillis        = 0;            // Global millis() timer
unsigned int          sampleCounter         = 0;            // Sensor measurement counter
unsigned int          samplesSaved          = 0;            // Log file sample counter
unsigned long         unixtime;
time_t                t, alarmTime;
tmElements_t          tm;

// ------------------------------------------------------------------------------------------------
// Data transmission unions/structures
// ------------------------------------------------------------------------------------------------
// Union to transmit Iridium Short Burst Data (SBD) Mobile Originated (MO) message
typedef union
{
  struct
  {
    uint32_t    unixtime;             // Date and time in time_t format           (4 bytes)
    int16_t     extTemperature;       // Mean external temperature (°C)           (2 bytes) (extTemperature * 100)
    int16_t     intTemperature;       // Mean internal temperature (°C)           (2 bytes)
    uint16_t    humidity;             // Mean humidity (%)                        (2 bytes) (humidity * 100)
    uint16_t    windSpeed;           // Resultant mean wind speed 1 (m/s)        (2 bytes) (windSpeed * 100)
    uint16_t    windDirection;       // Resultant mean wind direction 1 (°)      (2 bytes)
    uint16_t    windGust;            // Wind gust speed 1 (m/s)                  (2 bytes) (windGust * 100)
    uint16_t    windGustDirection;   // Wind gust direction 1 (°)                (2 bytes)
    uint16_t    voltage;              // Minimum battery voltage (mV)             (2 bytes) (voltage * 1000)
    uint16_t    transmitDuration;     // Debugging variable                       (2 bytes)
    uint16_t    iterationCounter;       // RockBLOCK data transmission counter      (2 bytes)
  } __attribute__((packed));                                                      // Total = 24 bytes
  uint8_t bytes[24];
} SBDMESSAGE;

SBDMESSAGE message;
size_t messageSize = sizeof(message); // Size (in bytes) of data to be stored and transmitted
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

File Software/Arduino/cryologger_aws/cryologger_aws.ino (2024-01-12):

/*
  Title:    Cryologger - Automatic Weather Station (AWS)
  Date:     October 16, 2023
  Author:   Adam Garbo
  Version:  1.3.1
  License:  GPLv3. See license file for more information.
    
  Description:
  - Code configured for an automatic weather station to be
  deployed in Ottawa, Canada that will serve as a test unit.

  Components:
  - Ground Control RockBLOCK 9603
  - Maxtena M1621HCT-P-SMA antenna
  - Adafruit Feather M0 Adalogger
  - Adafruit Ultimate GPS Featherwing
  - Adafruit BME280 Temperature Humidity Pressure Sensor
  - Adafruit LSM303AGR Accelerometer/Magnetomter
  - Pololu 3.3V 600mA Step-Down Voltage Regulator D36V6F3
  - Pololu 5V 600mA Step-Down Voltage Regulator D36V6F5
  - Pololu 12V 600mA Step-Down Voltage Regulator D36V6F5
  - SanDisk Industrial XI 8 GB microSD card

  Sensors:
    - RM Young 05103L Wind Monitor
    - Vaisala HMP60 Humidity and Temperature Probe
    - Maxbotix MB7354 Ultrasonic Sensor

  Comments:
  - Sketch uses 100048 bytes (38%) of program storage space. Maximum is 262144 bytes.
*/

// ----------------------------------------------------------------------------
// Libraries
// ----------------------------------------------------------------------------
#include <Adafruit_BME280.h>        // https://github.com/adafruit/Adafruit_BME280 (v2.2.2)
#include <Adafruit_LSM303_Accel.h>  // https://github.com/adafruit/Adafruit_LSM303_Accel (v1.1.6)
#include <Adafruit_Sensor.h>        // https://github.com/adafruit/Adafruit_Sensor (v1.1.9)
#include <Arduino.h>                // Required for new Serial instance. Include before <wiring_private.h>
#include <ArduinoLowPower.h>        // https://github.com/arduino-libraries/ArduinoLowPower (v1.2.2)
#include <IridiumSBD.h>             // https://github.com/sparkfun/SparkFun_IridiumSBD_I2C_Arduino_Library (v3.0.6)
#include <RTCZero.h>                // https://github.com/arduino-libraries/RTCZero (v1.6.0)
#include <SdFat.h>                  // https://github.com/greiman/SdFat (v2.2.2)
#include <sensirion.h>              // https://github.com/HydroSense/sensirion
#include <Statistic.h>              // https://github.com/RobTillaart/Statistic (v1.0.4)
#include <TimeLib.h>                // https://github.com/PaulStoffregen/Time (v1.6.1)
#include <TinyGPS++.h>              // https://github.com/mikalhart/TinyGPSPlus (v1.0.3)
#include <Wire.h>                   // https://www.arduino.cc/en/Reference/Wire
#include <wiring_private.h>         // Required for creating new Serial instance

// ----------------------------------------------------------------------------
// Define hardware and software versions
// ----------------------------------------------------------------------------
#define SOFTWARE_VERSION      "1.3.1"
#define HARDWARE_VERSION      "0.4"
#define ROCKBLOCK_VERSION_3F  true

// ----------------------------------------------------------------------------
// Define unique identifier
// ----------------------------------------------------------------------------
char UID[5] = "TST";

// ----------------------------------------------------------------------------
// Data logging
// ----------------------------------------------------------------------------
#define LOGGING         true  // Log data to microSD

// ----------------------------------------------------------------------------
// Debugging macros
// ----------------------------------------------------------------------------
#define DEBUG           true  // Output debug messages to Serial Monitor
#define DEBUG_GNSS      true  // Output GNSS debug information
#define DEBUG_IRIDIUM   true  // Output Iridium debug messages to Serial Monitor
#define CALIBRATE       false // Enable sensor calibration code

#if DEBUG
#define DEBUG_PRINT(x)            SERIAL_PORT.print(x)
#define DEBUG_PRINTLN(x)          SERIAL_PORT.println(x)
#define DEBUG_PRINT_HEX(x)        SERIAL_PORT.print(x, HEX)
#define DEBUG_PRINTLN_HEX(x)      SERIAL_PORT.println(x, HEX)
#define DEBUG_PRINT_DEC(x, y)     SERIAL_PORT.print(x, y)
#define DEBUG_PRINTLN_DEC(x, y)   SERIAL_PORT.println(x, y)
#define DEBUG_WRITE(x)            SERIAL_PORT.write(x)

#else
#define DEBUG_PRINT(x)
#define DEBUG_PRINTLN(x)
#define DEBUG_PRINT_HEX(x)
#define DEBUG_PRINTLN_HEX(x)
#define DEBUG_PRINT_DEC(x, y)
#define DEBUG_PRINTLN_DEC(x, y)
#define DEBUG_WRITE(x)
#endif
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

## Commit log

2020-12-10 Fix bug in battery voltage calculation
2022-04-22 Update to sensor code
    Add mapFloat function
2022-04-22 Upload KiCad design files
    [Cryologger AWS-B_Cu.gbl, Cryologger AWS-B_Mask.gbs, Cryologger AWS-B_Paste.gbp, Cryologger AWS-B_Silkscreen.gbo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]
2022-04-23 Fix KiCad design error
    [Cryologger AWS.kicad_pcb, Cryologger AWS.kicad_sch]
2022-04-25 Minor updates
    Improve code commenting and printing functions. Continue development on sensor code.
2022-04-26 Limit variables to be transmitted and add 1/10 voltage divider code
2022-04-28 Minor updates
    Standardize variable names. Begin adding wind sensor code. Increase multisampling.
2022-05-01 Add 3D printing files
    [F Mount v3.stl]
2022-05-02 Update 3D printing files
    [Mount.stl]
2022-05-02 Update test code and switch to manual ADC calibration and correction
2022-05-02 Major updates to prepare code for deployment
    Add additional variables that can be configured via Iridium SBD MT messages. Begin work on adding battery voltage threshold check. Add checks for GNSS RTC sync code.
2022-05-03 Minor updates
    Removed battery voltage function from ISBD callback in previous push due to it crashing the GNSS.
2022-06-09 Add sensor code
2022-06-10 Add support for additional sensors
    Code for Davis Instruments 7911 anemometer.
2022-06-17 Update PCB to v0.2
    Move KiCad and Gerber files into specific version folders.
    [Cryologger AWS-B_Cu.gbl, Cryologger AWS-B_Mask.gbs, Cryologger AWS-B_Paste.gbp, Cryologger AWS-B_Silkscreen.gbo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]
2022-07-01 Minor updates
    Change LED blink function to reference other pins.
2022-07-01 Add support for new sensors
    Added code for additional environmental sensors. Updated related statistics code. Prepared code for deployment testing.
2022-07-01 Add calibration code
    Add ADC calibration code and function to determine gain and offset.
2022-07-14 Update and rename ASSEMBLY.md to OPERATION.md
2022-07-22 Create folders for KiCad design iterations
    [Cryologger AWS-B_Cu.gbl, Cryologger AWS-B_Mask.gbs, Cryologger AWS-B_Paste.gbp, Cryologger AWS-B_Silkscreen.gbo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]
2022-07-23 Add KiCad prototype design files
    [Prototype.kicad_pcb, Prototype.kicad_sch]
2022-09-02 Add v0.3 design
    Organize KiCad files by version.
    [Cryologger AWS-B_Cu.gbl, Cryologger AWS-B_Mask.gbs, Cryologger AWS-B_Paste.gbp, Cryologger AWS-B_Silkscreen.gbo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]
2022-12-04 Standardize code relating to power
2022-12-04 Improve code commenting
    Begin adding wiring descriptions to sensors.
2023-01-16 Minor updates
    Added PIN_LED_RED definition to replace LED_BUILTIN.
2023-01-22 Add delay to GNSS power enable
    Improved code comments.
2023-01-22 Remove DPS310 code and standardize code
    Renamed alarmInterval to sampleInterval. Continued work on standardizing AWS and ITB code repositories. Improved code commenting.
2023-01-25 Minor updates to KiCad files
    Changed text on silkscreen and removed ground from hole pads.
    [Cryologger AWS-B_Cu.gbl, Cryologger AWS-B_Mask.gbs, Cryologger AWS-B_Paste.gbp, Cryologger AWS-B_Silkscreen.gbo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]
2023-01-30 Improve code commenting
    Added additional logging variables. Adjusted ADC calibration. Various updates to prepare code for deployment in Igloolik, Nunavut in 2023.
2023-02-08 Create Bulkhead Hole Pattern.pdf
2023-02-08 Update hole patterns
2023-02-10 Create Bulgin Hole Pattern Keyed Drawing.pdf
2023-02-17 Add iterations of 3D-printed enclosure components
    [Antenna Arm v1.stl, Antenna Arm v2.stl, Antenna Arm v3.stl, Antenna Arm v4.stl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]
2023-04-03 Create Bulgin Hole Pattern 2x3.pdf
2023-04-03 Create Bulgin Hole Pattern 2 x 3 Drawing v2.pdf
2023-04-06 Create Bulgin Hole Pattern 2 x 2.pdf
2023-04-06 Update Bulgin Hole Pattern 2 x 2.pdf
2023-04-08 Create Inner Panel Hole Pattern.pdf
2023-04-08 Create Anemometer Mount Hole Pattern.pdf
2023-04-19 Add ADC calibration values
2023-04-29 Update library version numbers
    Set ADC calibration values to default
2023-06-27 Update PCB to ensure compatibility with RockBLOCK v3.F hardware revision
    Added through-hole N-MOSFET for use with TN0702N3-G, which is required to control the on/off logic of the RockBLOCK v3.F. Organized KiCad files. Removed unnecessary backup files.
    [Cryologger AWS-B_Cu.gbl, Cryologger AWS-B_Mask.gbs, Cryologger AWS-B_Paste.gbp, Cryologger AWS-B_Silkscreen.gbo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]
2023-06-29 Set ADC calibration values to default
2023-06-29 Improve test code commenting
    Added more detailed descriptions of sensor wiring diagrams.
2023-06-29 Improvements to sensor test code
    Improved code commenting. Carried over pin definitions used in deployment code.
2023-06-29 Reenable pin power for wind direction measurement
2023-06-29 Add support for Maxbotix 7354 ultrasonic sensor
    Updated all related code to support the Maxbotix sensor, including logging, debugging, and statistics.
2023-06-29 Prepare code for deployment
    Code configured for deployed on Ellesmere Island during the 2023 field season. Added support for Maxbotix MB7354 ultrasonic sensor. Improved code commenting. Reverted sample interval back to unsigned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
2023-07-17 Remove archive files
    Deleted extraneous design files.
    [Antenna Arm v1.stl, Antenna Arm v2.stl, Antenna Arm v3.stl, Antenna Arm v4.stl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]
2023-07-17 Create archive folder for KiCad design files
    [Cryologger AWS-B_Cu.gbl, Cryologger AWS-B_Mask.gbs, Cryologger AWS-B_Paste.gbp, Cryologger AWS-B_Silkscreen.gbo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]
2023-07-17 Revert documentation to Arduino IDE 1.8.x
    Arduino 2.1.x still (July 2023) has too many bugs and is lacking key functionality that makes it a viable solution for end-users.
2023-07-19 Configure code for deployment
    Changed battery voltage function to return float value. Improved code commenting.
2023-10-20 Upload and update 3D-printed enclosure STL files
    [Enclosure Bottom.stl, Enclosure Top.stl]
